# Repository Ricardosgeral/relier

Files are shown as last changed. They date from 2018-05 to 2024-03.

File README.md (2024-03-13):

# *relier - acquisition system*
### Open {*re*}design of an acquisition system for {*l*}aboratory tests on {*i*}nternal {*er*}osion in soils

Project developed by [*Ricardo Correia dos Santos*](https://www.linkedin.com/in/ricardons/) at
[Laboratório Nacional de Engenharia Civil - *LNEC*](http://www.lnec.pt/en/), in Lisbon, Portugal

***relier AS*** is an open 'low budget' acquisition system (hardware and software), that automatically
collects data from multiple analog and digital output sensors, which are commonly used in laboratory tests on soil erosion. 

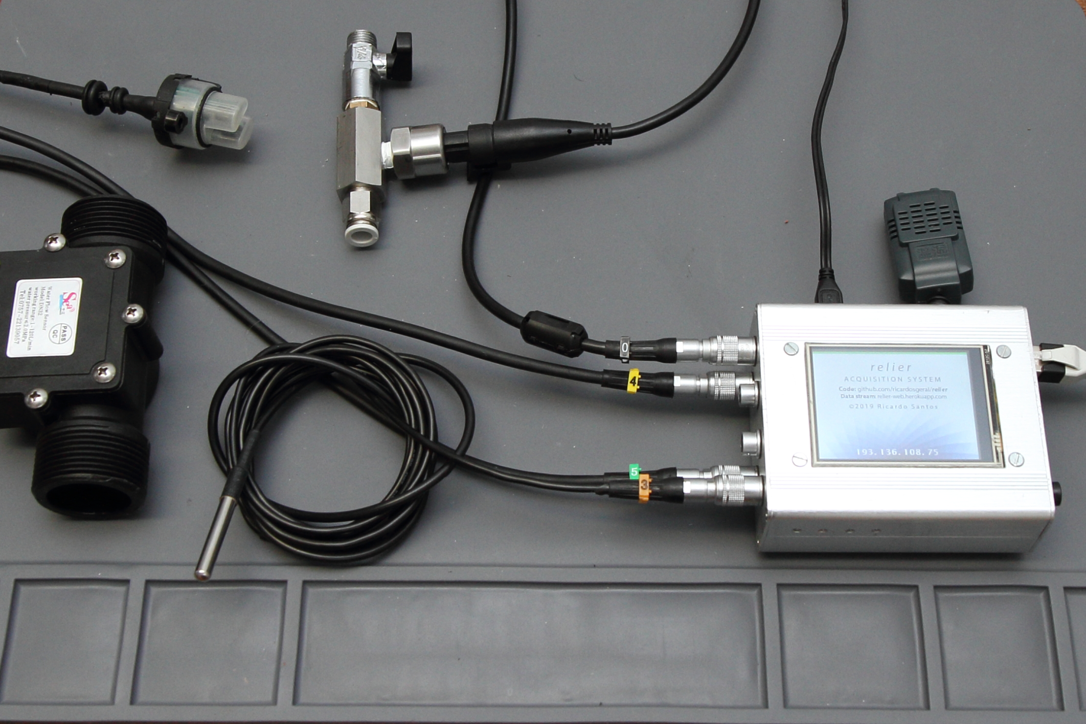
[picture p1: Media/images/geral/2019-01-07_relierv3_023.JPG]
relier


### Some project videos

| Sensors overview and GUI |  Assembly of acquisition system|
|--------------------------|--------------|
| GUI (https://youtu.be/-2fSeosClVY)|  GUI (https://youtu.be/6blSNBFLsIU)                              |

GUI (https://www.youtube.com/watch?v=ju51FE9KWwY)

### Is this for me?
If you need to do a similar project, you just need to have some DIY skills, for scrapping some materials, figuring out 
how to assemble some things together, and investigate how some components work.
The instructions given here should also be taken more like guidelines based on "what I can do with the materials I have". If 
you do not have the exact same hardware components 
(sensors, ADC, level shifter, touchscreen...), yours will surely work a little different, but as they should do the same 
things, there will be similarities too. You may have to adjust the code and/or the connections to meet your needs.

Feel free to contact me if you manage to get it working with different components, so these instructions can be improved 
and be more helpful. 

## 1. Hardware

The hardware components required to make the ***relier*** *acquisition system* are indicated in this chapter. 
Instructions about the way those components are connected are presented.
For reference, some links and prices of each component are indicated.

The *Hardware* is composed by the: 

+ ***Aquisition box*** (*server*, *touchscreen*, *custom PCB HAT* and *connection plugs*);
+ ***Sensors*** (4 with analog outputs and 3 with digital outputs).

### 1.1. Aquisition Box

The main items of the *acquisition box* are the following:
 
 + ***Server***: *Raspberry Pi 3 model B*;
 + ***2.8" Touchscreen***: *Nextion HMI display*;
 + ***Custom PCB HAT***: made specifically for this project ([details about the PCB design](https://github.com/Ricardosgeral/relier/blob/master/README.md#14-custom-pcb-raspberry-pi-hat)).
 
All these main components are placed inside an aluminum enclosure box, in which openings were made, for the power supply, display, and connections. 
Peripheral inputs to collect sensors data, and peripheral outputs (USB ports) to storage sensors data, are also available. 
The acquisition box is powered solely through the power supply connected to the Raspberry Pi (output: DC5V, 2A). 

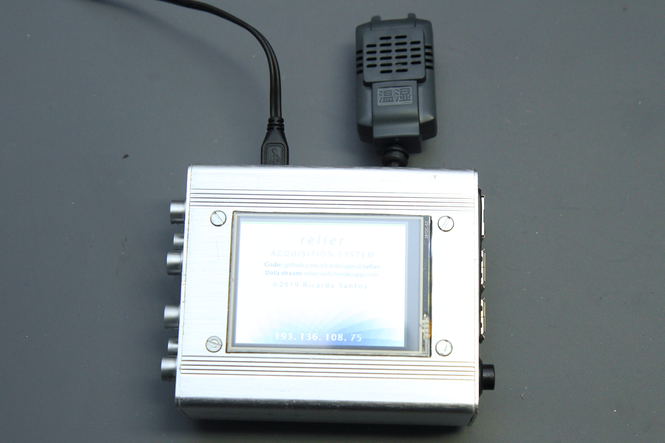
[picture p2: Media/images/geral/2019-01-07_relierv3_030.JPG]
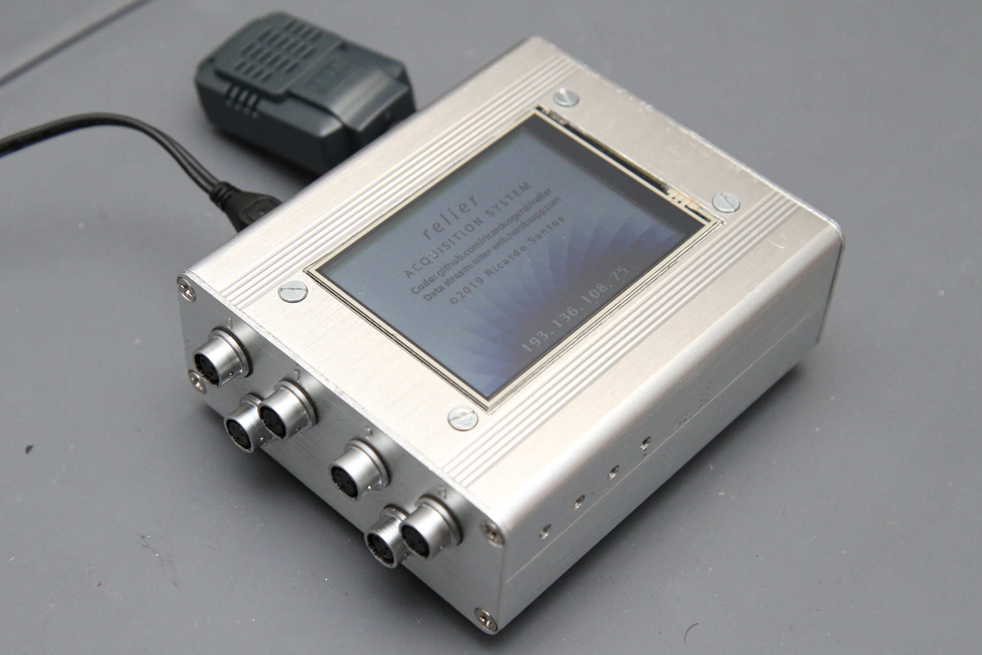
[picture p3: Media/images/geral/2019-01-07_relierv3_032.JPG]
|   |   |
|----------------------------------------|----------------------------------------|
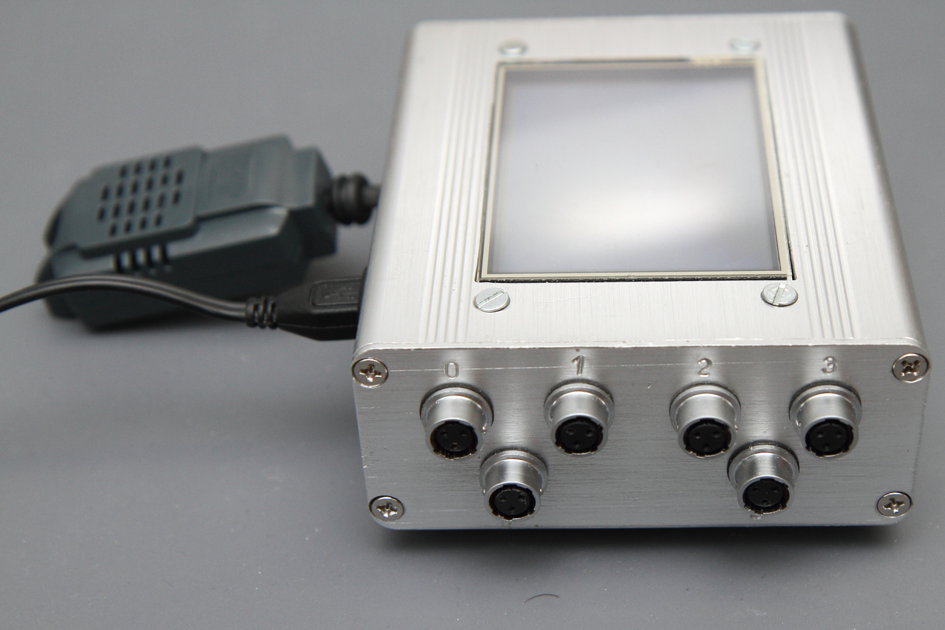
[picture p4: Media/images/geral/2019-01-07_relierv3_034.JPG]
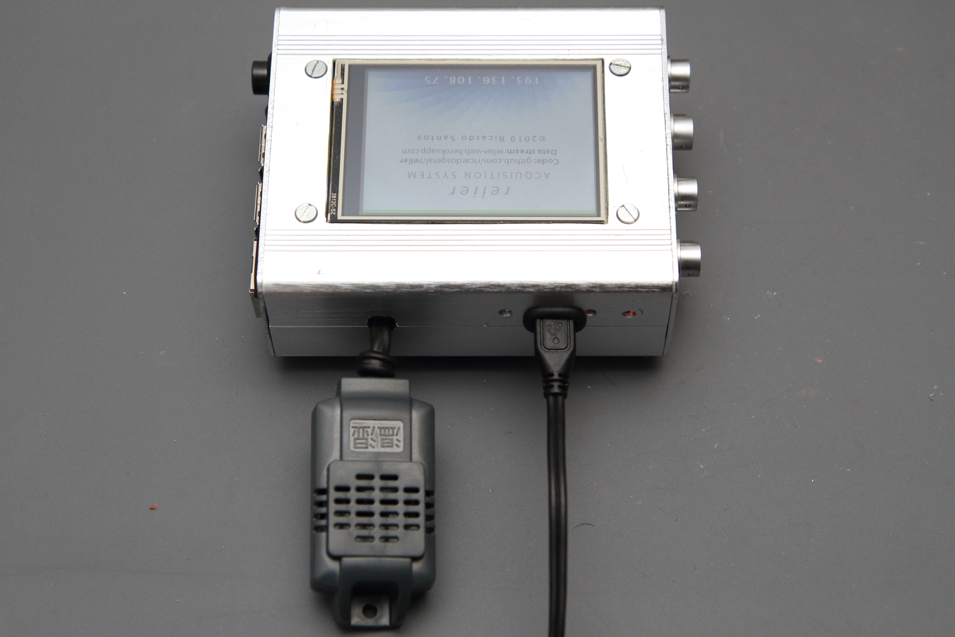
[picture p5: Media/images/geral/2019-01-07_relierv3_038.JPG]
|   |   |
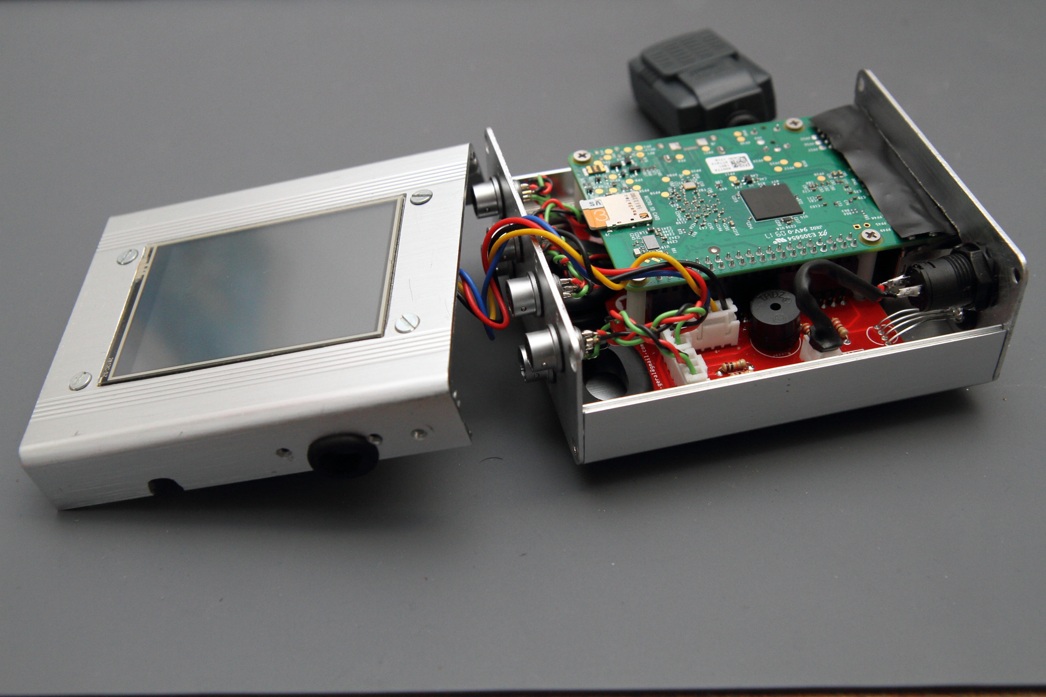
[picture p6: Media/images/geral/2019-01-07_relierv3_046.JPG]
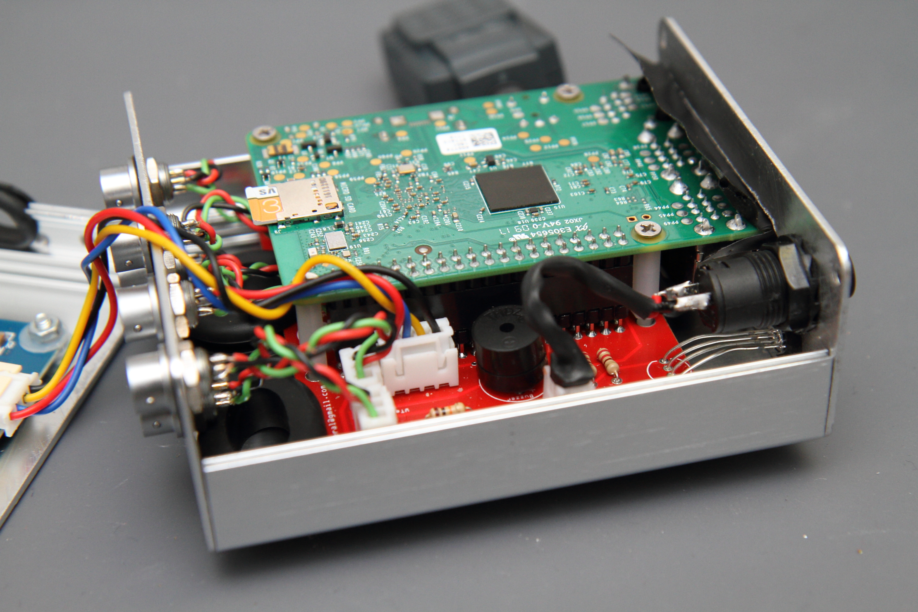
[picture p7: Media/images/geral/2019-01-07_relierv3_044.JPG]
|   |   |

https://i.imgur.com/RYcSZy1.jpg

You can find more pictures and an overview video in the [Media folder](https://github.com/Ricardosgeral/relier/tree/master/Media) of this GitHub repository.

### 1.2. Sensors

The ***relier*** *acquisition system* is prepared to simultaneously collect data from the following ***'low cost' sensors***:

+ **Channels 0-2**    : Analog pressure transducer sensor (Piezometric water pressure);
+ **Channel 3**       : Waterproof DS18B20 Sensor (Water temperature);
+ **Channel 4**       : Analog turbidity sensor (Water turbidity);
+ **Channel 5**       : Turbine flow Sensor (Water flow); and
+ BME280 sensor (Air temperature, humidity and pressure).

Most of the sensors are connected using the 6 mini aviator (circular) plugs that are linked to the custom PCB HAT. 
An exception is the *BME280* chip, which can be soldered directly to the custom PCB or using a short 4 wires cable. 
This last option is preferable, because, ideally, to monitor the ambient air temperature/humidity/pressure, 
the *BME280* should be placed outside the AS box (or at least, inside the box, but near large openings), 
to avoid the heat generated by the touchscreen and by Raspberry Pi!

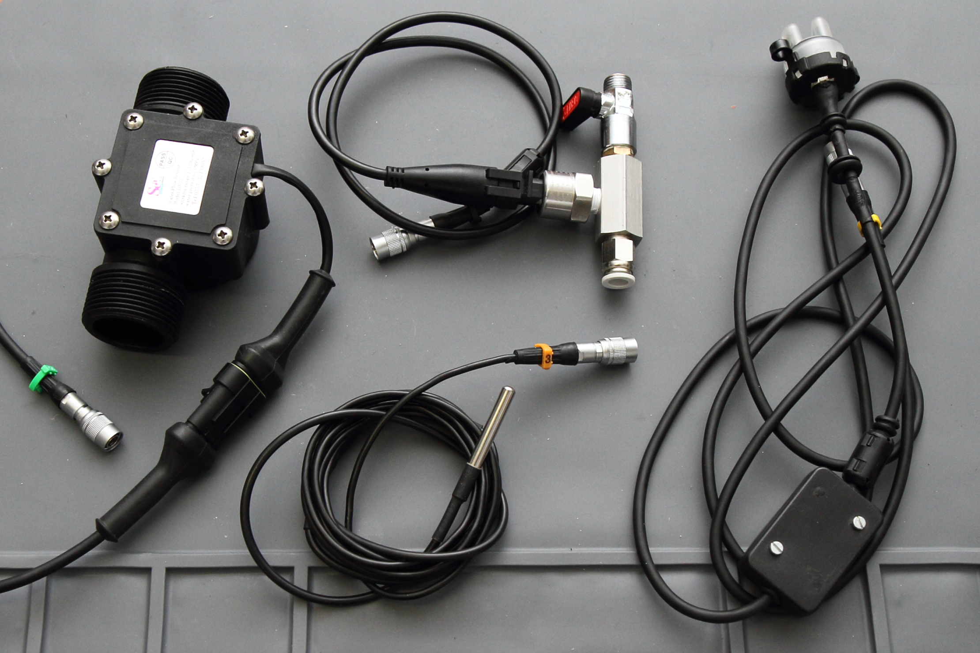
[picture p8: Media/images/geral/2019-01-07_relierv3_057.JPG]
sensors


**Note**:
***relier*** was designed to use low budget sensors. Thus, initially, only allowed the use of a turbine type flowmeter. 
However, since LNEC laboratory owns an Eletromagnetic type flowmeter ([Danfoss MAGFLO 5000](http://apps.watersurplus.com/techlib/Fluidyne/Fluidyne_Flowmeter_Mag1100_Mag3100_spec_D499.pdf)),
the software was adapted to also allow its use (communication via USB serial port of the Raspberry Pi).
Please beware that such devices are much expensive (1500-2000 €) than turbine flowmeters (< 20 €). 
The user should choose, in each test, one of these types of flowmeter.

The following table indicates the advantages and drawbacks of each type of flowmeter allowed. 

**Flowmeter type** |                                        |**Advantages**                                   | **Drawbacks**                                                              |
-------------------|----------------------------------------|-------------------------------------------------|----------------------------------------------------------------------------|
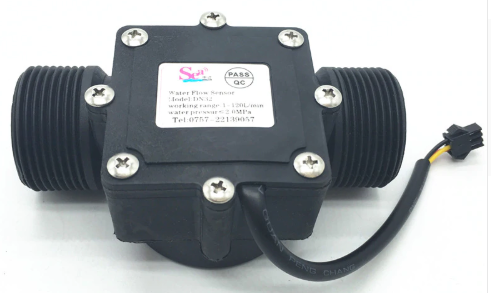
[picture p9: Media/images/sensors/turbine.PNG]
Turbine            |   |Cheap; Fast response to sudden drop/rise of flow | Low accuracy for low flow rates (may be even unable to detect low flow)    | 
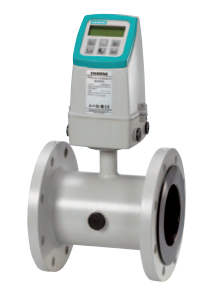
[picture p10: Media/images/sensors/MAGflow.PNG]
Eletromagnetic     |   |Better accuracy, even for low flow rates         | Expensive; Somewhat smother variation of flow, for sudden drop/rise of flow|

### 1.3. Bill of materials (BOM)

The following tables show the bill of materials (BOM) of the items used in ***relier*** **AS**, as well as their main specs and indicative prices (in January 2019).

#### Acquisition Box

| **Qt**  | **€/un*** | **Ʃ €** | **Photo**                                   | **Description**                                                                                                                                                                                                        | Notes                                                                               |
|---------|----------|----------|---------------------------------------------|------------------------------------------------------------------------------------------------------------------------------------------------------------------------------------------------------------------------|-------------------------------------------------------------------------------------|
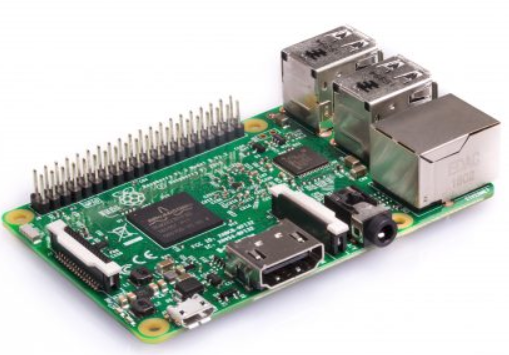
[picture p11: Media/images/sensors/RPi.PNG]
| 1       | 35       | 35       |            |[Raspberry pi 3B](https://www.raspberrypi.org/products/#buy-now-modal)                                                                                                                                                  | Server                                                                              |
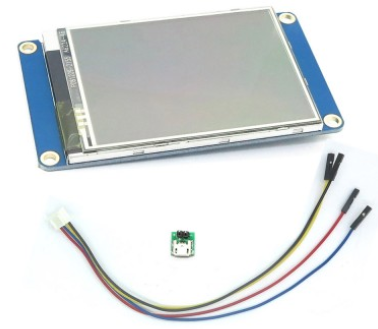
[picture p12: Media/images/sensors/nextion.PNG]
| 1       | 16.2     | 16.2     |        |[Nextion HMI touch display 2.8"](https://www.itead.cc/nextion-nx3224t028-1933.html)                                                                                                                                     | Graphical User Interface (GUI)                                                      |
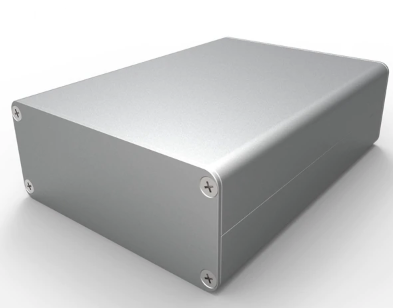
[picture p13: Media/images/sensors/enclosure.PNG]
| 1       | 6.2      | 6.2      |      |[Aluminium enclosure box (88x38x100mm)](https://www.aliexpress.com/item/Free-shipping88-38-100mm-width-x-high-x-length-aluminum-extrusion-box-profile-enclosure-for-PCB/32800855972.html?spm=a2g0s.9042311.0.0.Wvmz38)  | Aluminium enclosure box                                                             |
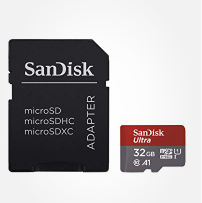
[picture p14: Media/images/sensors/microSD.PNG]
| 2       | 10       | 20       |        |Micro SD card (>16GB)                                                                                                                                                                                                   | One for the raspberry pi and another for the Nextion display (during installation)  |
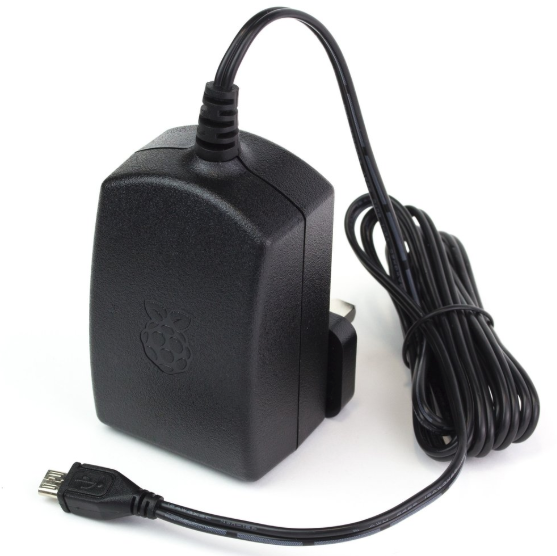
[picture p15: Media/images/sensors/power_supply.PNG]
| 1       | 8        | 8        |   |[Raspberry Pi Power Supply](https://www.raspberrypi.org/products/raspberry-pi-universal-power-supply)                                                                                                                   | Power up the raspberry pi and the sensors                                           |
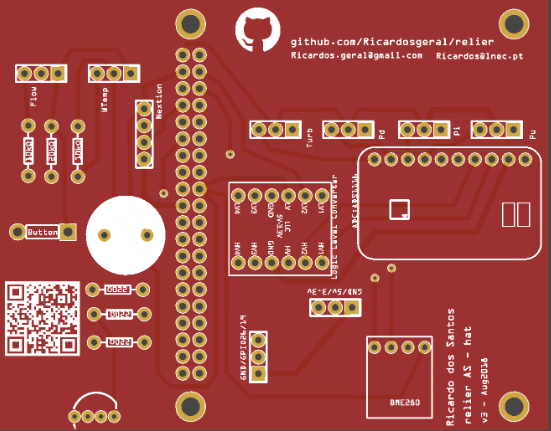
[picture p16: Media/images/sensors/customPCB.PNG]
| 1       | 1        | 1        |      |[**Raspberry pi Hat - Custom PBC**](https://www.pcbway.com/project/shareproject/Relier_Acquisition_system___for_Rasoberry_pi3_b_.html)**:**                                                                             | Interlinks server, touchscreen and the sensors                                      |
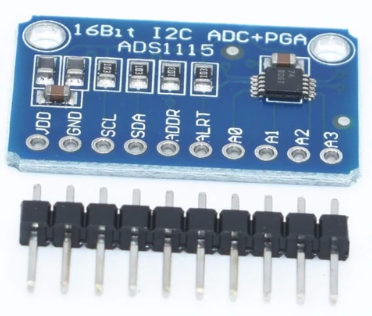
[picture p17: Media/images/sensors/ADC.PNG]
| 1       | 1.4      | 1.4      |            |► [16 Bit I2C ADS1115 Module ADC 4 channel with Pro Gain Amplifier](https://www.aliexpress.com/item/16-Bit-I2C-ADS1115-Module-ADC-4-channel-with-Pro-Gain-Amplifier-RPi-1PCS/32817162654.html)                         | Analog to Digital conversion for analog sensors                                      |
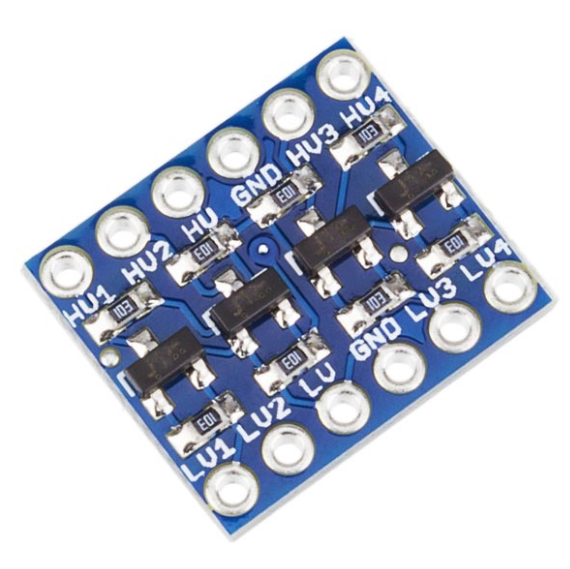
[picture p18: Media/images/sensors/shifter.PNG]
| 1       | 0.3      | 0.3      |        |► [Logic Level Shifter Bi-Directional 5V to 3.3V](https://www.aliexpress.com/item/5PCS-Logic-Level-Shifter-Bi-Directional-For-Arduino-5V-to-3-3V-Four-Way-Two-Way/32827270848.html)                                    | Required for stability, since ADS1115 requires 5V and Raspberry I2C pins use 3.3V    |
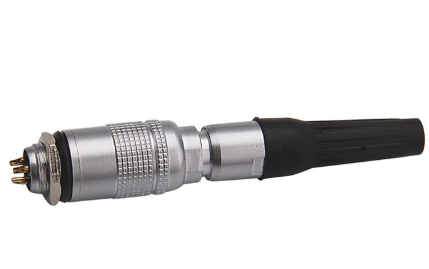
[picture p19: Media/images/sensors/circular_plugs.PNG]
| 6       | 3.8      | 22.8     | |► [8mm Male & Female Connector miniature Aviation Plug M8 Circular Socket+Plug](https://www.aliexpress.com/item/1PCS-AP049-YC8-2-3-4-5-6-7Pin-8mm-Male-Female-Connector-miniature-Aviation-Plug/32845374887.html)      | Connection of the sensors to the acquisition box                                     |
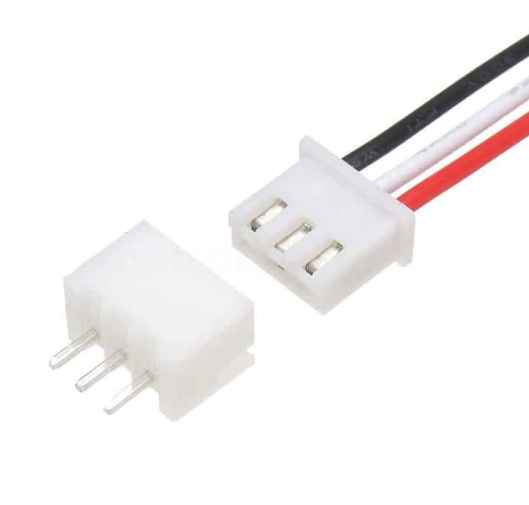
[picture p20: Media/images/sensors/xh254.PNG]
| 6       | 0.2      | 1.2      |          |► [XH2.54 3-Pins connectors Male for PCB - Header+Housing+Terminal](https://www.aliexpress.com/item/XH2-54-2P-3P-4P-5P-6P-7P-8P-9P-10P-11P-12P-13P-14P-15P/32793262315.html)                                           | Connection to the custom PCB                                                         |
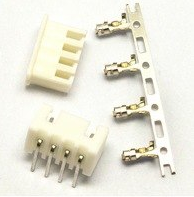
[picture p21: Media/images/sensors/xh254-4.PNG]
| 2       | 0.2      | 0.4      |        |► [XH2.54 4-Pins connectors Male for PCB - Header+Housing+Terminal](https://www.aliexpress.com/item/XH2-54-2P-3P-4P-5P-6P-7P-8P-9P-10P-11P-12P-13P-14P-15P/32793262315.html)                                           | Connection to the custom PCB                                                         |
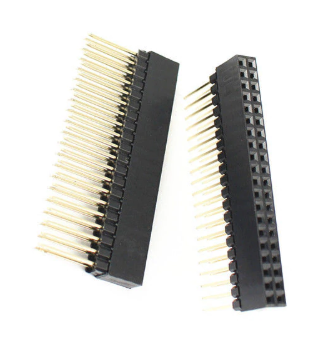
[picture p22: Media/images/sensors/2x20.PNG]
| 1       | 0.9      | 0.9      |           |► [PC104 2.54mm Pitch 2x20 Pin 40 Pin Female Double Row Long Pin Header Strip](https://www.aliexpress.com/item/2-Pcs-PC104-2-54mm-Pitch-2x20-Pin-40-Pin-Female-Double-Row-Long-Pin-Header/32805691836.html)            | Connection between Raspberry GPIO pins and the custom PCB                            |
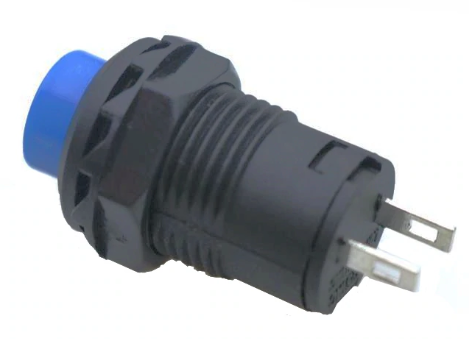
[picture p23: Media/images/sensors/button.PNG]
| 1       | 0.2      | 0.2      |         |► [Momentary pushbutton switch 3A Reset Button](https://www.aliexpress.com/item/10pcs-Momentary-Push-Button-Switch-12mm-Momentary-pushbutton-switches-3A-125VAC-1-5A-250VAC-Reset-Button/32802331189.html)             | Safe restart/shutdown button of the Raspberry Pi                                     |
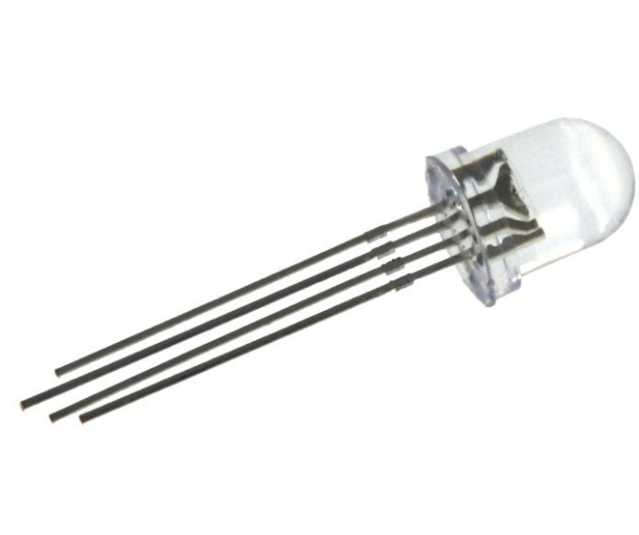
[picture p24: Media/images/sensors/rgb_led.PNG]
| 1       | 0.1      | 0.1      |        |► [5mm Through-Hole RGB LED](https://www.aliexpress.com/item/100pcs-lot-Transparent-Round-5mm-RGB-LED-Common-Anode-LED-Light-Emitting-Diode-Lamp/32278301731.html)                                                     | Indicative multicolor LED                                                            |
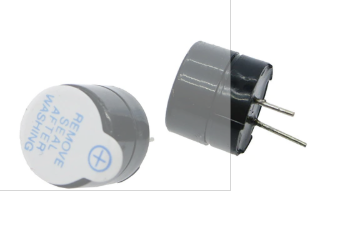
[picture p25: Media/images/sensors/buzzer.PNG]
| 1       | 0.1      | 0.1      |         |► [Active Buzzer Alarm 5 V](https://www.aliexpress.com/item/10pcs-5v-Active-Buzzer-Magnetic-Long-Continous-Beep-Tone-Alarm-Ringer-12mm-MINI-Active-Piezo-Buzzers/32914327679.html)                                     | Audible sound to alert for the end of a test                                         |
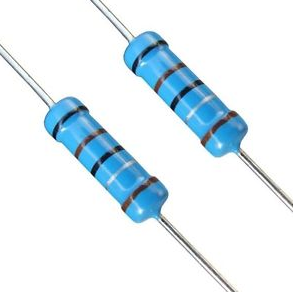
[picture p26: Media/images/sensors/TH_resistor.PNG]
| 3       | 0.02     | 0.06     |    |► [220 Ω carbon film resistor](https://www.aliexpress.com/item/100pcs-1-4W-Metal-film-resistor-1R-1M-100R-220R-330R-1K-1-5K-2-2K/32847011772.html)                                                                     | Protection of the RGB LED                                                            |
| 2       | 0.02     | 0.04     |    |► [10 kΩ carbon film resistor](https://www.aliexpress.com/item/100pcs-1-4W-Metal-film-resistor-1R-1M-100R-220R-330R-1K-1-5K-2-2K/32847011772.html)                                                                     | 1 used as voltage divider (turbine flowmeter) and other for water temperature sensor |
| 1       | 0.02     | 0.02     |    |► [20 kΩ carbon film resistor](https://www.aliexpress.com/item/100pcs-1-4W-Metal-film-resistor-1R-1M-100R-220R-330R-1K-1-5K-2-2K/32847011772.html)                                                                     | Voltage divider (turbine flowmeter)                                                  |
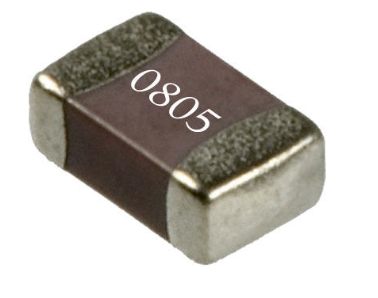
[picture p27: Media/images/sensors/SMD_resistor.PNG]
| 3       | 0.01     | 0.03     |   |► [0805 SMD 1/4W resistor 1MΩ](https://www.aliexpress.com/item/100Pcs-0805-SMD-1-4W-chip-resistor-0R-10M-0-10R-100R-220R-330R-470R-1K/32933956924.html)                                                                | Pull up resistors (to know when analog sensors are disconnected)                     |
| 6       | 0.1      | 0.6      |                                             |► 5 cm cable with 3 wires                                                                                                                                                                                              | Connection between mini aviator plugs and XH2.54 3 pin connectors                    |
| 1       | 0.1      | 0.1      |                                             |► 8 cm cable with 4 wires                                                                                                                                                                                              | Connection between BME280 and the custom PCB                                         |
|         |          | **115€** |                                             |                                                                                                                                                                                                                       |                                                                                     |

*The unitary prices don't include eventual shipping costs. 
For some items, it may be difficult to buy individual components and may be necessary to buy them in sets. 
There may exist cheaper alternatives. The prices indicated correspond to the components bought.

#### Low budget sensors

| **Qt**  | **€/un***| **Ʃ €** | **Photo**                                    |**Description**                                                                                                                                                                                                                    | Notes                                                                                          |
|---------|----------|---------|----------------------------------------------|---------------------------------------------------------------------------------------------------------------------------------------------------------------------------------------------------------------------------------- |------------------------------------------------------------------------------------------------|
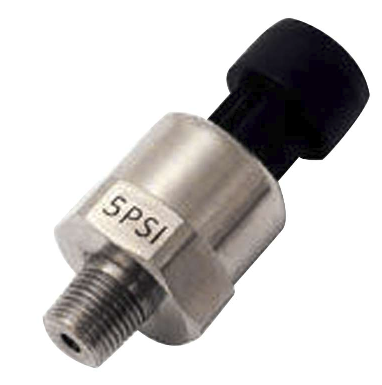
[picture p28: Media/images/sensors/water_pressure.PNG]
| 3       | 13       | 39      |  |[Analog Pressure Transducer Transmitter Sensor, 0-5psi 0.5-5V](https://www.aliexpress.com/item/1Pc-Pressure-Transducer-Sender-Stainless-Steel-for-Oil-Fuel-Air-Water-5psi-CSL2017/32814346612.html)                                | Measurement of water pressure at different levels (piezometers)                                |
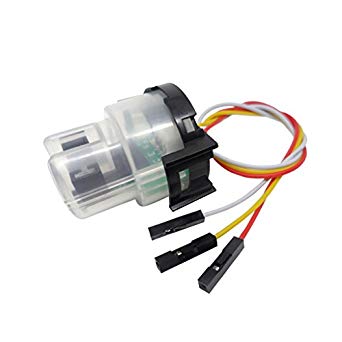
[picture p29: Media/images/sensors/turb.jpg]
| 1       | 9        | 9       |            |[Analog Turbidity Sensor, 5V 40mA](https://www.aliexpress.com/item/DFRobot-Gravity-Analog-Digital-Turbidity-Sensor-5V-40mA-DC-support-both-signal-output-compatible-with-arduino/32595773560.html)                                 | Measurement of the turbidity of effluent water                                                 |
| 1       | 13       | 13      |         |[Digital Turbine Flow Sensor, G5/4, 1.25", DN32, 1~120L/min](https://www.aliexpress.com/item/DN32-Water-Flow-Meter-Sensor-Switch-G5-4-Thread-Port-Industrial-Flowmeter/32567971320.html)                                           | Measurement of the water flow (the system also allows the use a electromagnetic type flowmeter)|
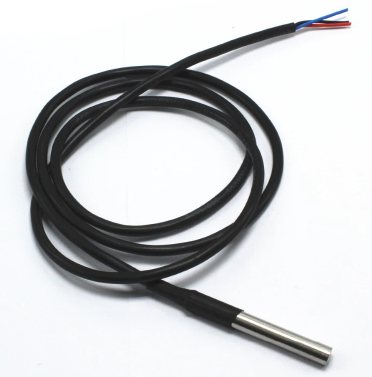
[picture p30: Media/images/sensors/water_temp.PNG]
| 1       | 1        | 1       |      |[Waterproof DS18B20 digital Temperature Sensor](https://www.aliexpress.com/item/1pcs-New-Digital-Temperature-Temp-Sensor-Probe-DS18B20-For-Thermometer-1m-Waterproof/1297739612.html)                                              | Measurement of the water temperature                                                           |
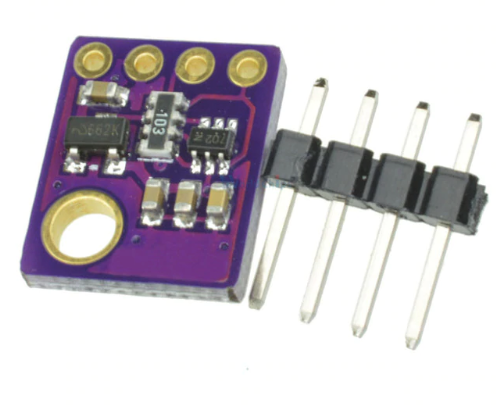
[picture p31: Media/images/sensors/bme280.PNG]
| 1       | 3        | 3       |          |[BME280 Digital Sensor, Humidity, Temp. and Barometric Pressure Sensor](https://www.aliexpress.com/item/3In1-BME280-GY-BME280-Digital-Sensor-SPI-I2C-Humidity-Temperature-and-Barometric-Pressure-Sensor-Module-1/32659765502.html)| Measurement of the atmospheric temperature, humidity and pressure                              |
|         |          | **65€** |                                              |                                                                                                                                                                                                                                   |                                                                                                |                                                                                      |

#### Total cost

The total estimated cost of the ***relier*** **AS** is about **180 €**, considering the use of low budget sensors. 
This value excludes costs related to other supplementary materials required for the assembly of the custom PCB (e.g. solder wire or DIY tools).

### 1.4. Custom *PCB* (Raspberry Pi HAT)
The design of the 2 layer's *PCB* was developed using the open-source software [Fritzing](http://www.fritzing.org/). 
The production files and the *.fzz* file are [here](https://github.com/Ricardosgeral/relier/tree/master/Fritzing). 
Latest version of *PCB* is v3.2 (November 2018). 
The *PCB* was produced/printed by [PCBWay company](https://www.pcbway.com/). 
You can order them a copy [here](https://www.pcbway.com/project/shareproject/Relier_Acquisition_system___for_Rasoberry_pi3_b_.html)).

Below, you can see images showing the circuits hooked in the breadboard and in the PCB, as well as the final 
aspect of each *PCB* layer individually. 
[Here](https://www.raspberrypi-spy.co.uk/2012/06/simple-guide-to-the-rpi-gpio-header-and-pins/#prettyPhoto/1/)
you can see the numbering of the 40 GPIO pins of the Raspberry Pi used.

**PCB: breadboard view**
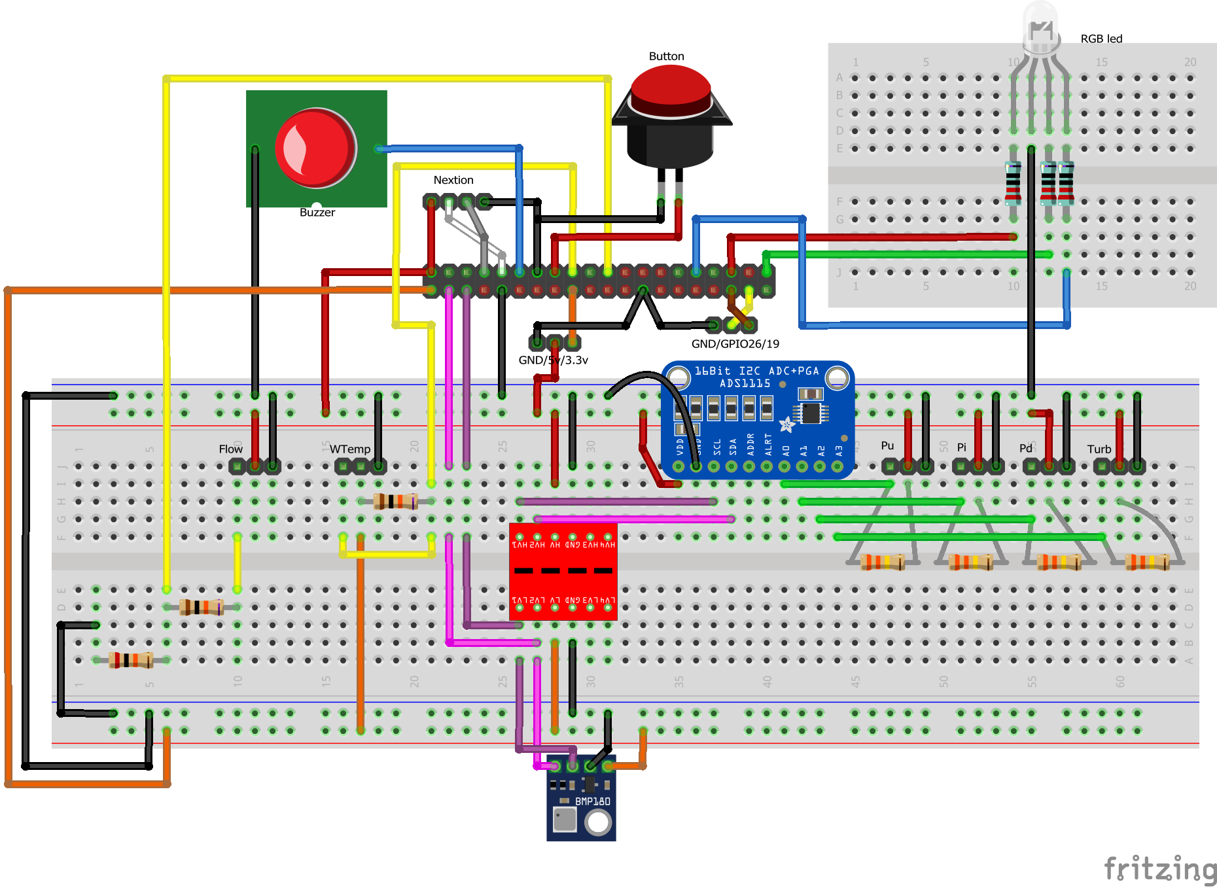
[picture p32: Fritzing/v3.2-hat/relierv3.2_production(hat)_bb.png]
Breadboard_image


| **PCB: bottom Layer**                                           | **PCB: top layer**                                       |
|-----------------------------------------------------------------|----------------------------------------------------------| 
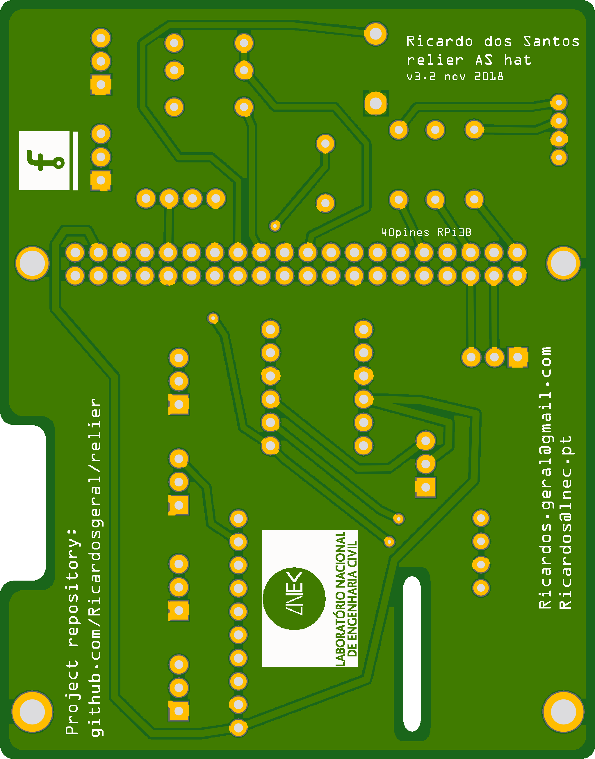
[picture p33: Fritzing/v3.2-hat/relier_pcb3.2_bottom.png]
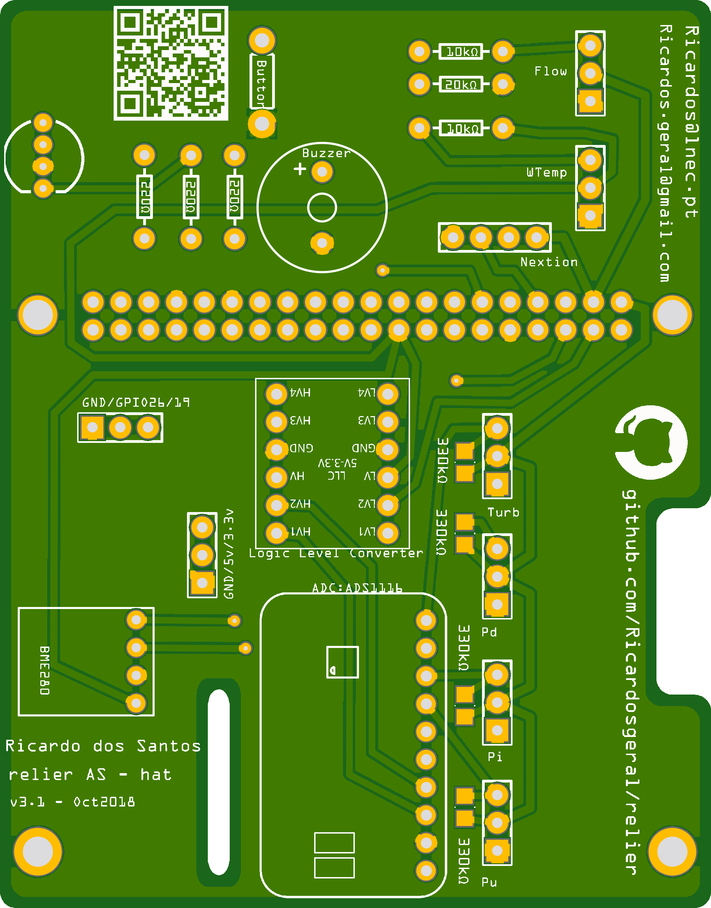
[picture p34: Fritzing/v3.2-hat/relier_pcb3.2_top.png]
|   |  |
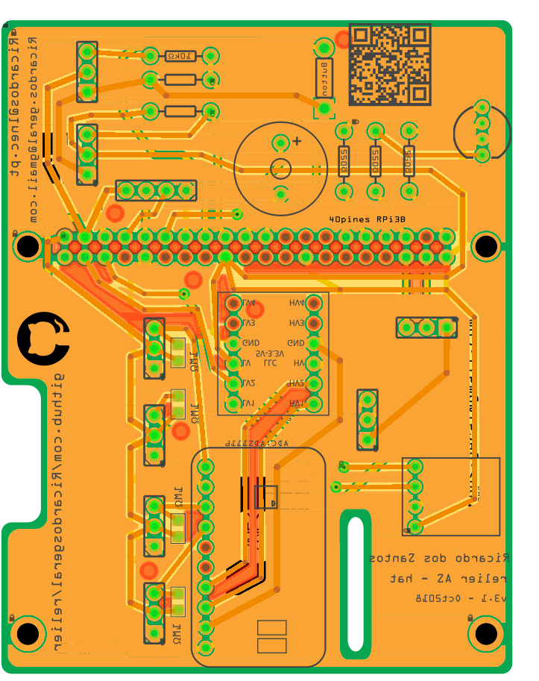
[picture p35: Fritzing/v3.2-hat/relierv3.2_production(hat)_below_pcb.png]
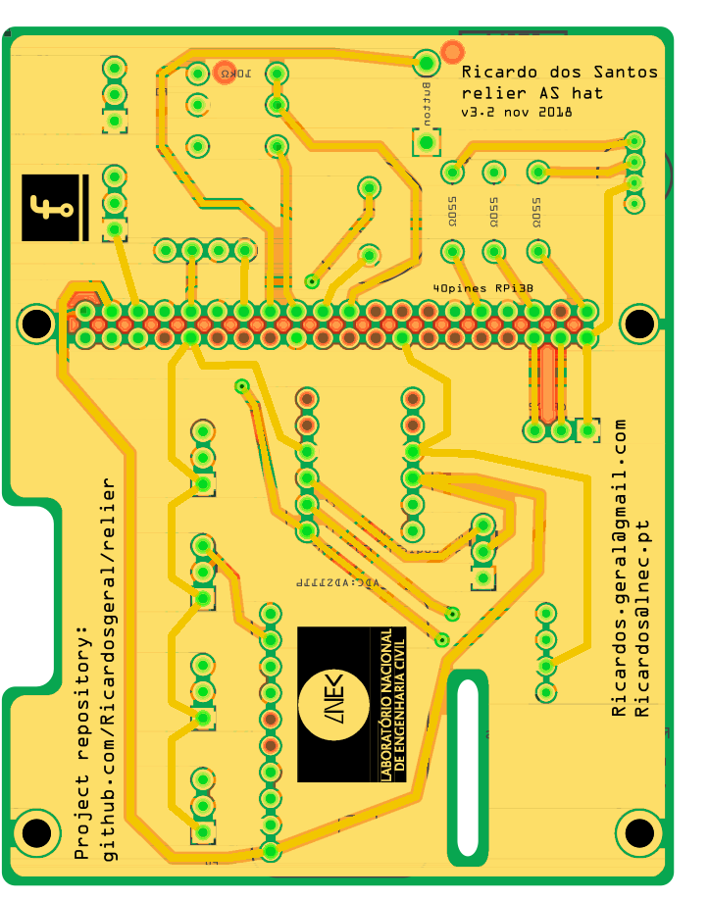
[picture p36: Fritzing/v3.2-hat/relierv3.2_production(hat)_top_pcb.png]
|   | |
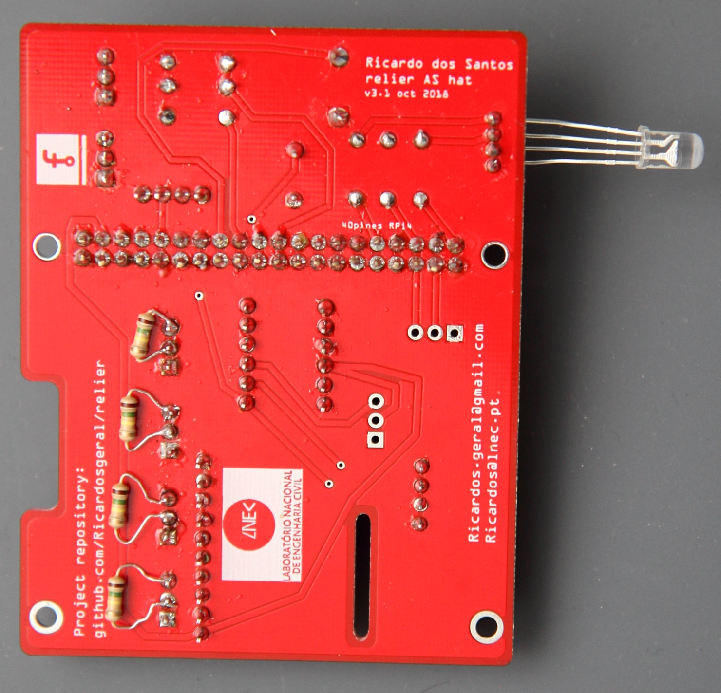
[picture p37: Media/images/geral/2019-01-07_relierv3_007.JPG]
PCBbottom_image
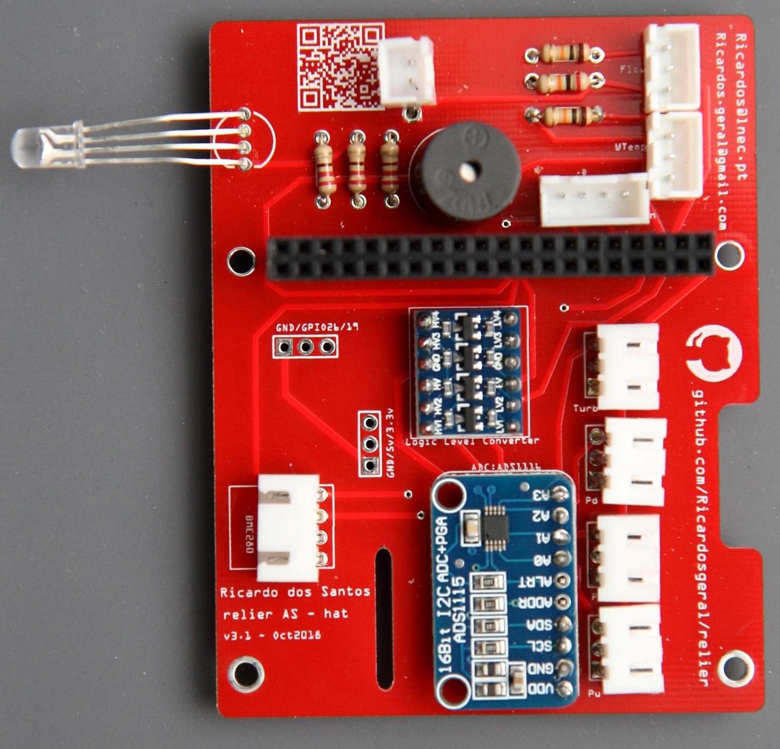
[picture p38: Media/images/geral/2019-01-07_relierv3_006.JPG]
PCBbottom_image
|   | |

**PCB: scheme**
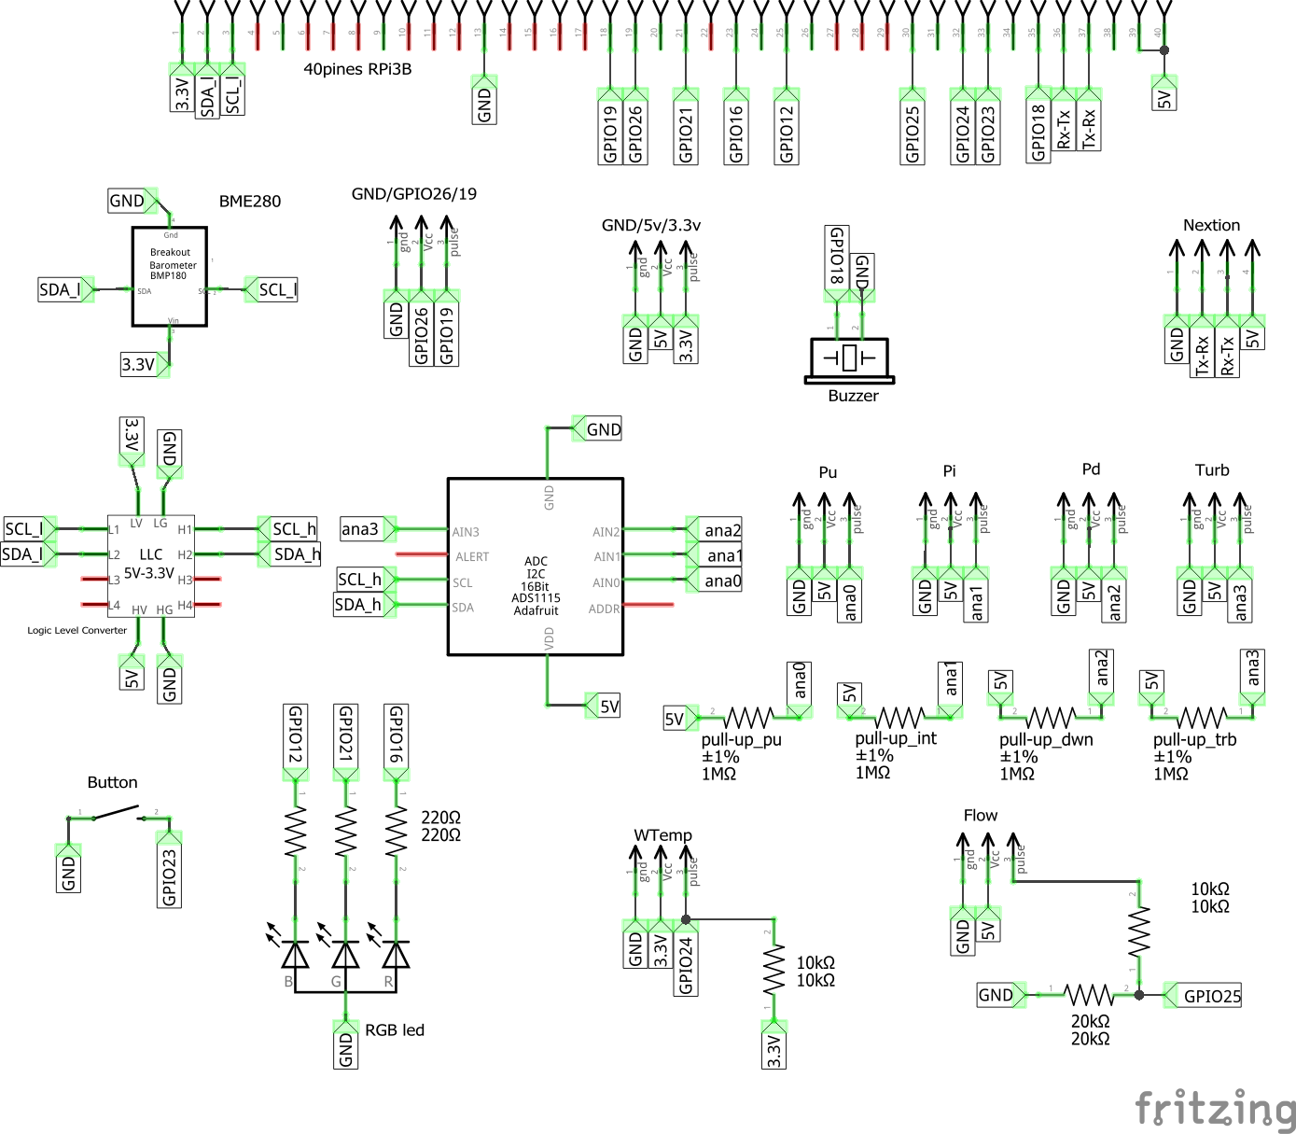
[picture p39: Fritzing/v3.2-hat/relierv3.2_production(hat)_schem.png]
PCB_image


### 1.5. Other components that may be useful for debugging
+ Breadboard(s)
+ [T-cobbler for raspberry pi](https://www.aliexpress.com/item/830-tie-points-MB102-breadboard-40Pin-Rainbow-Cable-GPIO-T-Cobbler-Plus-Breakout-Board-Kit-for/32673580640.html?spm=2114.search0104.3.9.6581309ai8NJdY&ws_ab_test=searchweb0_0,searchweb201602_1_10152_10151_10065_10344_10068_10342_10343_5722611_10340_10341_10698_10696_5722911_5722811_10084_5722711_10083_10618_10304_10307_10301_5711211_10059_308_100031_10103_10624_10623_10622_10621_10620_5711311_5722511,searchweb201603_32,ppcSwitch_5&algo_expid=3ed88c37-67f1-4fe2-a688-b3983db90ff7-1&algo_pvid=3ed88c37-67f1-4fe2-a688-b3983db90ff7&transAbTest=ae803_2&priceBeautifyAB=0)
+ DuPont jumper wires
+ Micro SD adapter
 
### 1.6. Additional tools required in the assembly of the Raspberry Hat and of the enclosure
+ Wire Stripper/Crimping tools
+ Soldering iron + solder wire
+ Tools to make the openings in the aluminum box (*eg* a mini Drill DIY set) 
+ Precision screwdriver set

## 2. Software

The  ***relier*** *acquisition system* is composed by two distinct but interconnected programs, particularly the:

+ **Server software**: *runs in the Raspberry Pi*, and performs the computation tasks, and
+ **Touchscreen software**: *runs in the Nextion device*, and is responsible by the interactivity between the end user and the server.

### 2.1. Server software: installation
The server is a Raspberry Pi 3 model B (it was also tested successfully with a RPi 3 B+).
 These instructions should be carried out after a fresh installation of *Raspbian* image in a Micro SD card 
(see [instructions](https://www.raspberrypi.org/documentation/installation/installing-images/README.md)). 
The server has been tested with [2018-11-15-raspian-stretch](http://downloads.raspberrypi.org/raspbian/images/raspbian-2018-11-15/). 
Most of the code is written in *Python v3.5.3*, and a few scripts are written in *Bash v4.4.12(1)*.

**Note:** If no monitor is available (*Raspberry Pi* headless setup), the following 4 simple steps are required to 
enable *SSH* on first boot. So, right after installing the Raspbian image in the  Micro SD card:
1. Create an empty file (in Windows use notepad, in a Linux terminal use command *touch*, in Mac use TextEdit).
2. Save the file with name: ***ssh*** (preferentially with no extension, but *ssh.txt* should also work).
3. Copy or move that file into the ***root*** of the Micro SD card, where Raspbian image is installed.
4. Insert the Micro SD card into the *Raspberry Pi*, and power it on.

Access the *Raspberry Pi* directly (if you have a monitor), or via *SSH* (for example, using [*Putty*](https://www.putty.org/)). 
In this last option, you will require an internet connection, and need to know the local IP attributed to the *Raspberry Pi* ! 
The default login parameters should be:

   username: `pi`   
   password: `raspberry`

It is recommended to change the password after first boot, since *SSH* is enabled! For that write down in the terminal

    $ passwd 
    
and choose your new password.

Now, if you haven't done it yet, you need to connect the *Raspberry Pi* to the internet (via Ethernet cable or [WiFi](https://www.raspberrypi.org/documentation/configuration/wireless/wireless-cli.md)).  
Then, in the terminal, run the following sequential commands:
    
    $ cd /tmp && wget https://raw.githubusercontent.com/Ricardosgeral/relier/master/bash/raspbian-post-install.sh
    $ sudo chmod +x raspbian-post-install.sh && sed -i 's/\r//' raspbian-post-install.sh
    $ sudo ./raspbian-post-install.sh

Prepare a big cup of hot tea, since this can take some minutes! The raspberry should reboot automatically!

**Note:** During installation of the server, [VNC](https://www.realvnc.com/en/raspberrypi/) is also enabled, 
case you want to use it. 

#### Google Credentials

***relier AS*** has the ability to send the main test results to google sheets, but, for that, it requires some configurations.
If you don't need this feature you can skip it.

After reboot of the RPi, you need to get your *json* file with your Google Signed credentials.
First, you need to create a project in the developer console and enable some APIs (follow steps 1 to 4 from these [instructions](https://pygsheets.readthedocs.io/en/latest/authorizing.html#)), 
then, get the *Signed credentials* (follow steps 5 and 6 from these [instructions](https://pygsheets.readthedocs.io/en/latest/authorizing.html#signed-credentials)). 
*Copy* your Signed credentials, then, do:

    $ sudo nano /home/pi/relier/service_creds.json
    
and *Past* the Signed credentials. `Ctrl+X`, then `y` and finally `Enter` to save file.

    $ sudo reboot

And that's it, after reboot, the *Raspberry Pi* is set properly. 
However, you still need to install the **Touchscreen software**!

### 2.2. *Touchscreen* software: installation

The graphical user interface (GUI) runs on a [*Nextion*](https://nextion.itead.cc/) smart touchscreen, 
also referred as an *HMI - Human Machine Interface*. 
Note that, this device does not work like typical TFT or HDMI monitors. 
A code needs to be developed and uploaded to the device using a Micro SD card. 
The connection between *Nextion device* and the *Raspberry Pi* is made via 
[*Serial UART*](https://www.allaboutcircuits.com/technical-articles/back-to-basics-the-universal-asynchronous-receiver-transmitter-uart/), 
that is, via serial communication in pins GPIO14 (TXD) and GPIO15 (RXD) (in all Raspberry models).

The GUI needs to be developed in the [Nextion Editor](https://nextion.itead.cc/resources/download/nextion-editor/) (free software - only for windows!).
Follow the [Nextion Editor Guide](https://nextion.itead.cc/editor_guide/) to learn how to work with it. 
I've provide the file [*relier.HMI*](https://github.com/Ricardosgeral/relier/blob/master/Nextion/HMI/relier.HMI) 
developed for this project. The next picture shows the Nextion Editor with the project file.

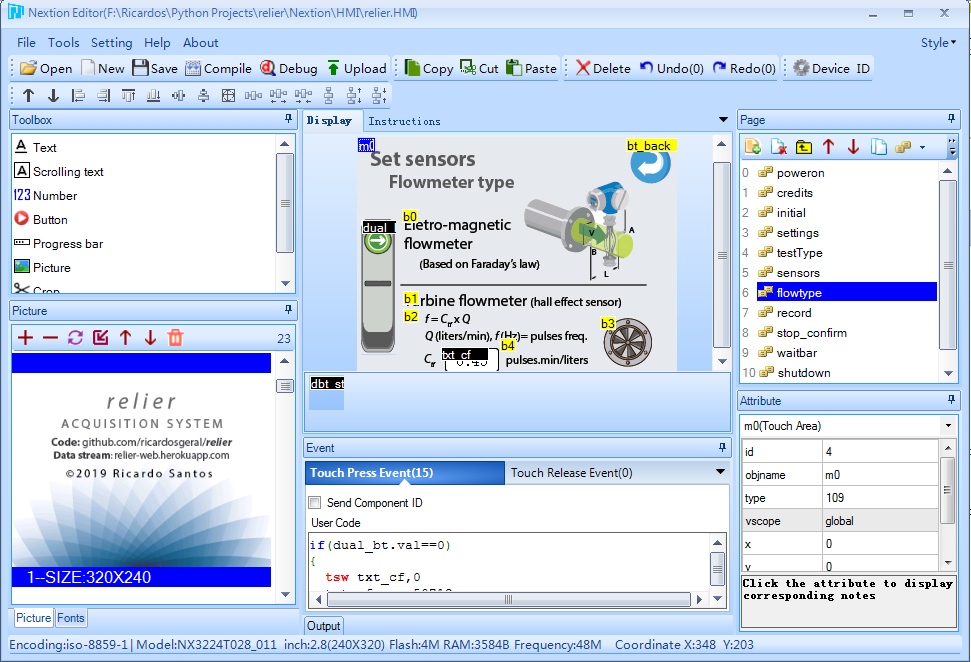
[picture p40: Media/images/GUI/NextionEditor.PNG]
NextionEditor


To upload the code into *Nextion device touchscreen* follow these steps:

1. Open the [*relier.HMI*](https://github.com/Ricardosgeral/relier/blob/master/Nextion/HMI/relier.HMI) file
with the Nextion Editor.
2. Press the *Compile* icon in the first top bar, and check that there are no errors.
3. Go to *File > Open build folder* and copy the *relier.tft* file produced by the editor (that has the code). 
4. Past the file into a formatted micro SD card. I recommend using the windows format tool, 
to ensure the card is empty. Don't forget to safe eject the sd card.
5. Disconnect the power supply to *Nextion*.
6. Insert the micro SD card in the slot on the back of the device.
7. Reconnect the power supply to *Nextion*. You should see the *SD card update* status. 
When you see `Check data.. 100%`, the code was uploaded successfully.  
8. Disconnect again the power supply to the screen, and remove the micro SD card (it will not be necessary anymore).
9. In next start up, the software with the code, developed in the Nextion Editor, is running 
and the GUI is set on the touchscreen.

**Note:** Be very careful when buying the *Nextion* device. Confirm that you are not getting a *TJC* (for the Chinese market), 
which looks identical. 
*TJC* screens only work with the Chinese version of the Nextion Editor! You will need to learn Chinese to use it !!!!

## 3. Graphical User Interface (GUI): How to use
 
The *GUI* pages displayed in the touchscreen (*Nextion device*), and their usage, are shown next.
 
### *Connecting* page
page0

Right after a start up or reboot of the *Raspberry Pi*, you should see this **Connecting** black page. 
Waiting a while (tipically 20 seconds, but can vary from 15 to 60 seconds, depending on the pending OS services) 
you should see the **Credits** page. 
In that process you should see fast blink of the led (with purple color) placed in the AS box.

### *Credits* page

First, you will see a *red* flag on the top of the screen. Wait (less than 5 seconds).
After some server checks, the flag should then stay *green*, meaning that the server and touchscreen are working Ok. 
You can also see the local *IP address* of the server, 
which is useful in case you want to make a remote connection. 

| *not ready*: red flag                                    |  *ready*: green flag                                      |
|----------------------------------------------------------|-----------------------------------------------------------|
| page1_red | page1_green|

If the server is not connected to the internet, then the following message is displayed: `No internet connection`.

To update the IP status case the internet connection has been changed (e.g., insertion of an Ethernet cable, connection to WiFi, ...), 
wait a couple of seconds, then touch on the IP message (bottom of the screen). 
Touch anywhere else on the screen to go the **Main menu** page.
 
### *Main menu* page
page2
 
You have three options:
 1. ***Settings***: set the *test inputs* >> Redirects to **General settings** page.
 2. ***Sensors***: set the *calibration inputs* of water pressure sensors and choose flowmeter type >> Redirects to **Set sensors** page.
 3. ***Start***: initiate the test right away >> Redirects to **Sensors data record** page.
 
You can skip options 1 and/or 2, case you use the files
[*inputs.ini* ](https://github.com/Ricardosgeral/relier#5-inputs-file-inputsini), 
[*calibturb.txt*](https://github.com/Ricardosgeral/relier#calibturbtxt-file)
and you are confident that the calibration
parameters of the pressure sensors, specified in that file, are accurate enough. 
 
### *General settings* page
page3

Here, you can edit interactively the test inputs:
- *CSV filename* textbox - name of the CSV file were test data is saved.
- *Google Sheets* checkbox - select it, to send test data to Google Sheets during the test. Disable it if you haven't configured the google credentials.
- *Spreadsheet* textbox - name of the Google spreadsheet (worksheet name = *CSV filename*). Not used if *google sheets* checkbox is disabled.
- *email* textbox - email to where a link, to access the Google spreadsheet, will be sent. Not used if *google sheets* checkbox is disabled.
- *Test time* textbox - duration of the test, in minutes ( if 0 is selected → records data 'forever' or until user stops it).
- *Record* textbox - interval between records, in seconds.
- *Number* textbox - number of readings in each record interval (for analog outputs only).

Pressing the blue button on top-right corner goes back to **Main menu** page. 
There is also a blue button that allows the user to select the **Test type**.

### *Test type* page
page4

This page allows the selection of the type of test you want to perform.
Note that, selecting the option <Hole Erosion Test (HET)>,
***no*** data of the interface (middle) pressure sensor will be acquired, 
since HET only uses two pressure sensors (upstream and downstream).
If you select <**Other**>, a textbox is enabled for the user to give a name to the test type. 
In this case, test data from all sensors is recorded.

To go back to the **General settings** page, click the blue return button. 

### *Set sensors* page
page5

This page allows to see the sensor data (piezometric pressure, flow and turbidiy), which should be displayed every second.

It can also be used to set the calibration parameters of the analog pressure sensors and of the turbidity sensor. 

For the pressure sensors a linear relation, between the analog readings and the effective measurements, is assumed. 
***m*** and ***b*** are the calibration parameters.

The calibration of turbidity is made *exclusively* using the file *turbcalib.txt*. 
First line of this file is ignored and values should be separated by tab or spaces. 
Decimal separator should be a point (.), **not** a comma (,).

To edit the file, open a terminal and type:

    $ sudo nano /home/pi/relier/turbcalib.txt 

The following table indicates the units that should be considered for the calibration parameters.

| Sensors             | ***x*** (analog from ADC)    | ***y*** (measurements) | Relation y = f(x)      |
|:--------------------|:-----------------------------|:-----------------------|------------------------|
| Pressure transducer | voltage,V (*Volt*)           | pressure, p (*bar*)    | ***p = m V + b***      |
| Turbidity           | 0 to 32767 (15 bits >> 2^15) | turbidity (gr/liter)   | ***turbcalib.txt***    |

This page also includes:

a) ***Calibration* button**: to update readings after setting new input parameters.

If you modify  the *m* and *b* parameters of any of the sensors, you need to push the *Calibration* button, 
in order to see the influence on the pressure and/or turbidity values. 

b) ***Zeroing* button**: to make current sensor pressures equal to zero.

This functionality can be used to take into account the normal variations of the atmospheric conditions and the normal sensors drift over time.
To use it properly, it is necessary, first, to ensure that *no pressure* is applied to the sensors (besides the ambient pressure).

In such conditions, ideally, the readings from the pressure sensors should indicate null *mbar*. 
However, due to the influence of drift, barometric pressure, ambient temperature, humidity, and others, 
the most likely is that they are not zero. 

If you push the *Zeroing* button at this stage (*ie*, with no external pressure applied), 
you will get a *wait a few seconds* progress bar. After a few seconds, the readings will show up again,
and show the corrected values.
Now the piezometric pressures should be nearly null. The next figure exemplifies the '*zeroing*' procedure, 
which is done in all pressure sensors simultaneously.

zeroing

***Attention***: the '*zeroing*' process (when desired!) should be done at the beginning of each test, 
 since the history of the zero shift, *z*, is not (intentionally) remembered by the acquisition system after reboot. 

When you consider that the pressure sensors are conveniently calibrated, you can press the *back blue button* (top-right), 
which will send you to the **Main menu** page.

Pushing the *Home* button will send you to the **Credits** page.  
Pushing the *flowmeter icon* button will redirect the user to the ***Flowmeter type*** page 

### *Flowmeter type* page

This page allows to select between a turbine flowmeter and an Eletromagnetic flowmeter.

page6

If a turbine flowmeter is selected, the parameter ***Ctf*** should also be indicated (default value is 0.45).  
*f = Ctf x Q*, where *Q* (liters/min) is the flow rate and *f* (Hz) are the pulses frequency. 

Pressing the *back blue button* will bring the user back to ***Set sensors*** page, 
and changes to the flowmeter type are reflected in the flow rate value.

### *Sensors data record* page
page7

This page appears once the *Start* green button in **Main menu** is released. 
After a couple of seconds, the data being recorded appears in the screen and is updated at a constant rate (*interval* input parameter).

If 'Google Sheets' option has been selected, the first reading can take more than normal (due to the request to access the Google API).

Each time the acquisition system records a set of values, the LED will blink with a green color.

If you want to stop the test, prior to the test duration defined in settings, 
just press the *Red button*, which performs one more reading and then will redirect 
the user to the **Stop recording** confirmation page.

When the predefined test duration is achieved, the server stops acquiring the data. 
The buzz emits some sounds (SOS in morse code! :) ), and the screen is redirected to the *Credits* page.

**Note:** if you want to record data 'forever', set the *Test time duration* input parameter to **0**. 
Actually, it will not record indefinitely. *'Forever'* should be understood as 2 months (86400 minutes!).

### *Stop recording* page
page8

Here you confirm that you pressed the stop button, just in case! Pressing the:

- *Green button* >> stops recording data and directs to **Credits** page. 
- *Red button*   >> go back to **Sensors data record** page, and readings never stopped being registered.
 Buzzer should also alert for the end of the test.

### *Shut down* page

When the physical push button at the lateral side of the acquisition box is hold longer than 3 seconds, the Raspberry Pi shut downs automatically.

page9 

The user should unplug the power supply, after some seconds (> 10s).

## 4. Web live streaming of data from sensors

In GitHub repository [relier-web](https://github.com/Ricardosgeral/relier-web) 
you can find all the required files to deploy a *Python* application to the internet that allows web streaming of the test data recorded.
In that way you can live view the test results acquired by ***relier*** from any device connected to the internet 
(smartphone, tablet, laptop, ...). 
The acquisition system server should be connected to the internet before the start of the test.  

The picture below shows the the app layout, which is accessed at the site ***https://APP_NAME.herokuapp.com*** (you should choose the <APP_NAME>)
 
relier-web

## 5. Inputs file: *inputs.ini*

It is possible to set most of the test inputs by editing the file [*inputs.ini*](https://github.com/Ricardosgeral/relier/blob/master/inputs.ini). 
Editing the file avoids setting the inputs interactively in the touchscreen. 
For that, open a terminal and run the command:

    $ sudo nano /home/pi/relier/inputs.ini
     
and change the parameters as intended.

The structure of the *inputs.ini* file comprises 6 sections: [settings], [testtype], [analog], [flowmeter], [ip] and [path]. 
The last two sections are informative only, thus, their edition don't produce any effect!
An example of an *inputs.ini* file, with a description of the meaning of each parameter, is shown below.

#### Example of file *inputs.ini* 
```
[settings]
filename      = soil_X_n01   # <Name of the CSV file> and (if google_sheets = yes) <Worksheet of Google Spreadsheet>
google_sheets = yes          # <yes (y, yep, Yes, YES) or no (n, nop, No, NO)>  
googlesh      = tests_soilX  # <Name of the Google spreadsheet>
share_email   = my@email.com # <email to share access to the Google spreedsheet>
duration      = 180          # <Duration of the test in Minutes> duration = 0 will run 'forever'
interval      = 15           # <Interval between records in seconds>
no_reads      = 5            # <Number of readings per interval (analog sensors only)>: 
                             #  In this example an average between 15/5=3 values is made.

[testtype]
testtype      = 1            # <1 to 4>  1-HET; 2-FLET; 3-CFET; 4-OTHER
othername     = other_name   # < Name of the test type> only relevant when testtype = 4

[analog]                     # Equation of the straight lines for pressure sensors: y = m x + b
mu            = 0.0862       # <Upstream pressure sensor> [ pu(bar) = mu tension_u(Volts) + bu ] 
bu            = -0.0432
mi            = 0.0898       # <Interface pressure sensor> [ pi(bar) = mi tension_i(Volts) + bi ]
bi            = -0.0432
md            = 0.0898       # <Downstream pressure sensor> [ pd(bar) = md tension_d(Volts) + bu ]
bd            = -0.0432

[flowmeter]                  # Parameters about the flowmeter type
flowmeter_type = 1           # < 1 or 2> 1-Eletromagnetic;   2-Turbine  
cf = 0.45                    # Calibration parameter for the turbine flowmeter

[ip]
lastip     = 193.136.108.75  # Parameter is not editable! It's an indication of the server IP in the last test 

[path]
lastpath   = /srv/EROSTESTS/soil_Y_n01.csv  # Location where the results of the previous test were stored.
```

#### Additional notes

+ If the user changes the parameters in the interactive way, [*inputs.ini*](https://github.com/Ricardosgeral/relier/blob/master/inputs.ini) 
will be updated every time the, 
  + server begins to record data (green start button in **Main menu**), or
  + blue back button is released in **Set sensors** page.
+ In such cases, the parameters are kept and are set by default in the next test.
+ Note that the parameters in the *ini* file will not appear always in the same order! 
However, they will always appear in their respective sections. 
That is, for example, the parameter *interval* will always appear in section [settings], 
but may appear at any position inside its section.

## 6. Turbidity calibration 

The calibration of the turbidity sensor is made mixing successive portions of soil with a know quantity of water. 
The water used in calibration should of the same nature and chemistry of the one that will be used in the soil tests. 
The liquid should be agitated during all the calibration process, to avoid sedimentation of any suspended particles. 
This can be achieved easily using a portable magnetic stirrer. 

Since the turbidity probe is not waterproof, a calibration cup has been designed for safety reasons. 
The design of this calibration cup is available in [Thingiverse](https://www.thingiverse.com/thing:3299997). 
The calibration cup shown in the pictures below was 3D printed in PLA material. Feel free to (re)use the design.

|   |   |
|---|---|
|turbcalib | turbcalib|

**Procedure/Steps**

The steps and best practices to achieve a consistent calibration curve for the turbidity sensor are here presented. 
Below are some photos taken during the calibration for the finer fraction of a coarse soil (passing sieve #60, aperture of 6.3 mm)

|turbcalib |turbcalib |
|-----|------|
|turbcalib |turbcalib|

These are the main steps:
1. Place a know quantity of water (e.g. 500 ml) inside a beaker.
2. Place the beaker over a portable magnetic stirrer. Turn it on, and regulate the spinning in a way that the water is agitated, but without forming a visible vortex.
3. Place the calibration cup (with the sensor) floating in the water.
4. Connect the turbidity sensor to Channel 4 in the acquisition box, and start the system (i.e. connect the RPi to the power supply).
5. Register ***analog#*** of this channel. The register of this values can be done:
    + *Manually* - Navigate to [*Set sensor*](https://github.com/Ricardosgeral/relier/blob/master/README.md#set-sensors-page) page, 
and register the values shown in the turbidity section;
    + *Automatically* - Navigate to [*Sensors data record*](https://github.com/Ricardosgeral/relier/blob/master/README.md#sensors-data-record-page) page, 
and the ***analog#*** values are recorded to the adequate file (see [Data collection](https://github.com/Ricardosgeral/relier/blob/master/README.md#7-data-collection) section).  
6. Add a known mass of the selected soil (e.g. 0.1 grams) to the stirring water. Wait a fee seconds, and then register the new ***analog#*** values,
 which are expected to be smaller than those before adding the amount of soil.
Calculate the turbidity in grams/liter, dividing the cumulative mass of the soil by the total amount of water (e.g. 0.1 grams/0.5 liters = 0.2 l/g).
7. Repeat step 6 until the entire range of possible turbidity's is tested. As reference, it is considered that calibration process is finished when analog# is below 1000. 
8. Modify the file *calibturb.txt* with the tested pairs of *analog#* versus *turbidity* (g/l). This procedure is indicated next.

### Edition of *calibturb.txt* file

The file *calibturb.txt* allows to define a calibration curve for the turbidity analog sensor. 
For that, open a terminal and run the command:

    $ sudo nano /home/pi/relier/calibturb.txt

Pairs of **analog number** (0 to 32767) versus **turbidity** (grams/liter) should be introduced.

### Example of file *calibturb.txt* 
```
Analog#  grams/liter   # The first line is always ignored
29618	0
29586	0.025
29430	0.05
 ... (omitted values)
1154	34.5
 778    47.1
```
Below is a graphical representation of a calibration curve (made using tap water).

turbcalib

#### Additional notes for calibration accuracy and repeatability

- For each new turbidity being calibrated, it is always recommended to do an average of the recorded values. 
- Ensure that the probe (emitter and receiver) are submersed, and there are no air bubbles between them. Air bubbles influence strongly the readings. 
- Avoid direct sunlight on the turbidity probe during the calibration process. Direct sunlight is likely to alter readings. 
- The ambient light, water temperature and environment conditions (temperature, light and humidity) should be similar to those during the actual tests.
- If **analog#** is obtained automatically, the interval between readings is the one defined in [General settings](https://github.com/Ricardosgeral/relier/blob/master/README.md#general-settings-page) page.

## 7. Data collection
The *acquisition system box* handles the sensors and gets the data from them.  
The location where data will be collected is defined  by the user, and depends
on whether an internet connection is available, and whether a USB drive is plugged in.

### 7.1. No internet connection

Data is only saved locally in the *CSV* format and has two possible ways to go:
  
1. *No USB drive* is plugged in  >>
   Data are saved *only* on the micro SD card, inside folder **/srv/EROSTESTS**. 

2. A *USB is plugged in* >>
   Data are saved *only* on the **USB_root_directory**. 

#### Additional notes

- The name of the *CSV* file is defined by the user, either using:
   + the *touchscreen GUI*, in **General settings** page, or  
   + the *inputs.ini* file, modifying the parameter *filename*.
- Before removing a USB drive or the micro SD card it is ***strongly*** recommended to gently shutdown the *Raspberry Pi*, 
and unplug the power supply.
This will prevent corruption of the micro SD card and of the USB drive, and increase their life span. 
To silently disconnect the server you can either:
   + hold the *red pushbutton* in the back of the *acquisition system box* for more than *3 seconds* (if holden between 1 and 3 seconds, 
   the *Raspberry Pi* will reboot), or 
   + `$ sudo halt` in a *SSH* terminal session.
- If more than one USB drive is plugged in (not recommended !), data will be saved in the *first drive* being found.
- Data in the *CSV* files is ***never deleted*** automatically. If a file with the same name already exists in the USB drive or 
in the micro SD card, data is saved in the file but placed below the last row already there. This means that multiple tests may be collected 
in the same file (not desirable). It is preferable to set each test in an individual file.

### 7.2. Internet connection available (Ethernet or WiFi)

Data collection is also saved locally in *CSV* format. 
That is, if a USB drive is plugged in, data is saved to the USB drive, otherwise, data is saved to the server micro SD card.

However, ***in addition***, it is possible to send data to [Google Sheets](https://www.google.com/sheets/about/), if a valid 
*service_creds.json* file is provided (see instructions in *Software installation > server sofrware*).

#### How to enable 'Google Sheets'
1.  Select that option:
   - In the *touchscreen GUI* > *Settings* > activate the (only) checkbox, or
   - In *inputs.ini* file > ensure that *google_sheets = yes*.
   
2. Provide names for the *Spreadsheet* and for the *Worksheet*:
   - In the *touchscreen GUI* > *Settings*  > *Spreadsheet* (*Worksheet* name = *CSV filename*), or
   - In *inputs.ini* file > Spreadsheet name = *googlesh*, and Worksheet name = *filename*.

3. Provide a valid email, since a link to access the spreadsheet will be shared via email at the start of the test.
   - In the *touchscreen GUI* > *Settings* > Add email, or
   - In *inputs.ini* file > use parameter *share_email*.

#### Additional notes

- If the *Spreadsheet/Worksheet* provided by the user already exists, the data that was in that worksheet will be *deleted* (***Attention***). 
However, when a new Worksheet name is provided in an already existing Spreadsheet, a new sheet is added. 
This means that you can have a single Spreadsheet with different tests organized in different Worksheets (preferable).
- If there is no internet connection, data will not be, of course, sent to Google Sheets, 
even if you select the Google Sheets checkbutton (***Attention***). For debugging please see the 
[troubleshooting](https://github.com/Ricardosgeral/relier#troubleshooting) section. 
- If internet connection is lost during a test, the software will raise an exception and stop recording data to Google Sheets, 
but it will continue to record data locally (USB drive or micro SD card).
- Please be aware that, by choosing the 'Google Sheets' feature, the interval between readings chosen by the user 
will be increased a couple of seconds, due to the time required to request access the Google API. 
If you need an interval between readings smaller than 8 seconds, or you require an always constant interval between readings, 
please disable the 'Google Sheets' feature.

## 8. Achievements and reuse of *Python code*

- Use of the [*ADS1115*](https://www.adafruit.com/product/1085) *Analog to Digital Conversor (ADC)*, to acquire the analog outputs of the pressure sensors and turbidity sensor.
If you want to use another ADC (e.g., the [MCP3008 (10 bits)](https://www.adafruit.com/product/856), 
which is faster but less precise), the Python library will need, of course, to be replaced and the python code should be adapted.
- Use of the [*pigpio library*](http://abyz.me.uk/rpi/pigpio/) to get the readings from the turbine flowmeter (hall-effect sensor), using the function [callback](http://abyz.me.uk/rpi/pigpio/python.html#callback). 
More information [here](https://www.raspberrypi.org/forums/viewtopic.php?t=66445).
- *Use of threading (['thread-based parallelism'](https://docs.python.org/3/library/threading.html)), together with [Event objects](https://docs.python.org/3/library/threading.html#event-objects), in Python 3*. 
Threads are used in this project in three cases: 
   + In the handling of the results from *analog sensors*, for data 'stability'. Threads allow to do a mean over a certain period of time 
   with a shorter delay between samples. This can in some cases improve the data reliability. Thus, 
   the collection of readings from the ADC (ADS1115) is done using a [Thread Class object](https://docs.python.org/3/library/threading.html#thread-objects).   
   + Since *temperature sensors* take some time between reads (about 1 second), 
   the readings of those sensors is done in multi-tasking. 
   This ensures that the interval between readings is the one indicated by the user. 
   Treads are here also used as *Class objects*.
   + Detection of *serial communication* between the server and the Nextion touchscreen. 
   The server needs to check if the touchscreen is pressed, independently of being at the same time doing other tasks. 
   To achieve this it is used *Thread*, alongside with *Event*, both from the threading module. This achievement took me a while to master, and I believe it may be useful to others.
- *Use of Multiprocessing* (['Process-based parallelism'](https://docs.python.org/3/library/multiprocessing.html)). 
Multiprocessing is used to acquire data from the Eletromagnetic flowmeter via serial USB communication. [Value](https://docs.python.org/3/library/multiprocessing.html#multiprocessing.Value) method uses Shared memory to pass values between processes.
- Implementation of a [Ring buffer](https://www.oreilly.com/library/view/python-cookbook/0596001673/ch05s19.html), to avoid overflow of readings coming from the ADC chip.
- *Library for serial communication with the Nextion device in Python 3* (TX-RX, UART protocol). 
Unfortunately, until the day I'm writing this, a Python library to use Nextion touchscreen was not available.
There is a good library developed for Arduino, but I did not want to mix Python and *C* code. 
So, I've developed my own Nextion Library for Python 3 (which took me a while to achieve !).
This library is relatively simple to use, and has margin for improvement. 
You just need to look at the [*py3nextion_lib.py*](https://github.com/Ricardosgeral/relier/blob/master/py3nextion_lib.py),
and use it alongside with [*nextionApp.py*](https://github.com/Ricardosgeral/relier/blob/master/nextionApp.py) 
that has all the components (to be accessed by the server) defined in the Nextion Editor. 
Function *detect_touch()* in [main.py](https://github.com/Ricardosgeral/relier/blob/master/main.py)
is responsible for the continuous listening of the Nextion return bits, and the execution of for the following actions.
Of course, you need to know how to use the Nextion commands.
For that, see the [*instructions set*](https://nextion.itead.cc/resources/documents/instruction-set/).
- Use of the library [*pygsheets*](https://github.com/nithinmurali/pygsheets), alongside with 
library [*pandas*](https://pandas.pydata.org/index.html), to collect data from multiple sensors and send them to Google Sheets.  
- Use the library [*CSV*](https://docs.python.org/3.6/library/csv.html) to write the data (as dictionary) in rows.
- Use of the library [*configparser*](https://docs.python.org/3/library/configparser.html) to have a *.ini* file 
with the inputs.
- Use of the library [pyserial](https://pythonhosted.org/pyserial/), to read from the TX/RX (communication with the Nextion) and USB serial ports (communication with the Eletromagnetic flowmeter).
- Automatic detection when USB drives are plugged-in (mounted) or removed (unmounted).
 This also implies writing two rules in file *99-local.rules*.
- Combined Restart / Shutdown Button for Raspberry Pi 
(using a [*systemd service*](https://wiki.debian.org/systemd)) more info see [shutdown_button](https://github.com/scruss/shutdown_button): 
   + *Reboot*: hold the button more than half second but less than 3 seconds. The LED blinks with blue color and then the RPi reboots. 
   + *Shutdown*: hold the button more than 3 seconds. The LED blinks with red color and then the RPi shutdowns.
   Note, that the Raspberry Pi is still powered. 
 You still need to unplug the micro USB cable, to power off the server. 
 To restart the server after a shutdown, just power up the server again.
- Detection of the local *IP address* of the server (if connected to the internet).
- Start a python script right after start up or reboot of the server (*Raspberry Pi*), 
using [*crontab*](https://debian-administration.org/article/56/Command_scheduling_with_cron).
- Enable IC2 and 1-wire GPIO in file */boot/config.txt*.
- Enable pins 14(TX) and 15(RX) to use UART serial connection (where Nextion device is connected).  

## 9. Troubleshooting
 
- The following warning is expected: *'grep: /dev/fd/63: No such file or directory'* at the end of 
`$ sudo ./raspbian-post-install.sh`. Ignore it.
- Don't forget to obtain and replace the content of the file [*service_creds.json*](https://github.com/Ricardosgeral/relier/blob/master/service_creds.json), 
as indicated [above](https://github.com/Ricardosgeral/relier/blob/master/README.md#server-software-raspberry-pi), 
or the " Export to Google Sheets" feature will not work!
- The inspection of the **cronlog** file (`$ sudo nano /home/pi/relier/logs/cronlog`) may be helpful for detecting 
any eventual bugs during the software installation process, or during start up of the server, for example, 
to check if the Google credentials are correct!.
- *'Problem: Google signed Credentials'*. In this case, confirm that you have an internet connection,
and that you followed all 6 steps in installation of the server software. Don't forget to enable the 'Drive API' (step 4).
- If the Nextion touchscreen is not functioning properly or not working at all:
  + first, see the connections, in particular check that: RX (server) <-> TX (screen), and TX (server) <-> RX (screen); 
  + second, confirm that the baudrate is correct. By default nextion comes with 9600, but in program it is defined as 38400. This means that in first time
  the nextion needs to be set to that baud rate using file *pynextion_lib.py*.
  + third, ensure that *serial* is disconnected: `$ sudo raspi-config` > *5* > *P6 Serial* > *No*;
  + last, doing `$ ls -l /dev | grep serial` you should see *serial 0 >> ttyAMA0* (pins 14/15 in UART) and 
  *serial 1 >> ttyS0* (bluetooth in miniuart). By default UART is attributed to Bluetooth and miniuart to pins 14/15 (which has limitations). 
  That's why they are changed during the execution of 
  [*raspbian-post-install.sh*](https://github.com/Ricardosgeral/relier/blob/master/bash/raspbian-post-install.sh).
- To check if the *Analog-to-Digital Converter* (ADC - ADS1115 chip) and BME280 are properly connected via I2C, you can do 
*`$ sudo i2cdetect -y 1`*. 
 You should see a matrix with number ***48*** (ADS 1x15) and number ***76*** (BME280). 
 Otherwise, something is not connected correctly, or I2C protocol has not been enabled 
 (again, the bash file [*raspbian-post-install.sh*](https://github.com/Ricardosgeral/relier/blob/master/bash/raspbian-post-install.sh) should have done that !).
- If you want to check if the Linux service units running on reboot/shutdown are active, check their status.
 ```
 $ sudo systemctl status rcshut
 $ sudo systemctl status shutdown_button
 ```   
   `Ctr + D ` to leave the terminal.
- If you, by any reason (e.g., for debugging), need to stop all the python scripts that are running from startup of the server, 
open a terminal and execute:
 ```
 $ sudo pkill -9 python
 ```

## 10.  About the author and the *relier* project
I'm a Civil Engineer, with a [master degree](https://www.researchgate.net/publication/273715929_Enquadramento_das_analises_de_riscos_em_Geotecnia) 
in risk analysis in Geotechnical Engineering, and a [PhD](https://www.researchgate.net/publication/265396445_Experimental_investigation_on_limitation_of_the_progression_of_internal_erosion_in_zoned_dams?_sg=TYpuvUDlOEmsy1nkmycUNZZQmLHo34eFR1un5kQBsel1Ih6m8itcptNphw4q33ZLbFPsnKm5uX3PfaJmW1fljV7_goXnxDN4Ne4RwewR.OOCKioxBNPJoOd0B8BiFk4-Dqk849OZdMI_lxDR_IRduPQ88ovShdBBoVm34ZNhMTA_UT3M8PANv1KdYr7rMXg) 
on internal erosion in embankment dams.
 
Carrying out the [laboratory tests on internal erosion in soils](https://www.researchgate.net/publication/317742058_Limitation_of_the_progression_of_internal_erosion_in_zoned_dams), 
developed in my PhD, 
requires to simultaneously collect different types of measurements (water pressures, flow rate, temperature, turbidity, ...).
The measurements had to be registered by hand, in regular intervals, by two operators!! 
Such manual process is tedious and prone to errors.

So, I've decided to invest time developing a 'low budget' acquisition system (hardware and software) that could 
collect data automatically from multiple analog and digital output sensors. 
*relier* born this way!

Please note that I'm not an expert in informatics, in computing, nor in electronics.
I define myself as an enthusiastic self learner. 
All shown here was developed from my own research, mainly on forums, Github and other websites.
Thus, it is possible that some things (code, connections, methods...) could be optimized, or done in a different or a better way. 
Yet, ***relier*** *acquisition system* performs as intended.
You can report bugs, suggest enhancements, or even fork the project on [Github](https://github.com/Ricardosgeral/relier). 
All contributions are welcome.

## 11. Acknowledgements
My thanks to *António Timóteo* (LNEC-DG technician) for his work on cutting the openings in the acquisition aluminium box. 
Also, my thanks to *João Paixão* (LNEC-CIC technician) for soldering the smaller and more difficult parts 
(cup terminals of the mini aviator plugs and the pines in the ADC and of the level shifter).

## 12. License
Copyright (c) 2019 Ricardo Correia dos Santos

See the [license conditions](https://github.com/Ricardosgeral/relier/blob/master/LICENSE).

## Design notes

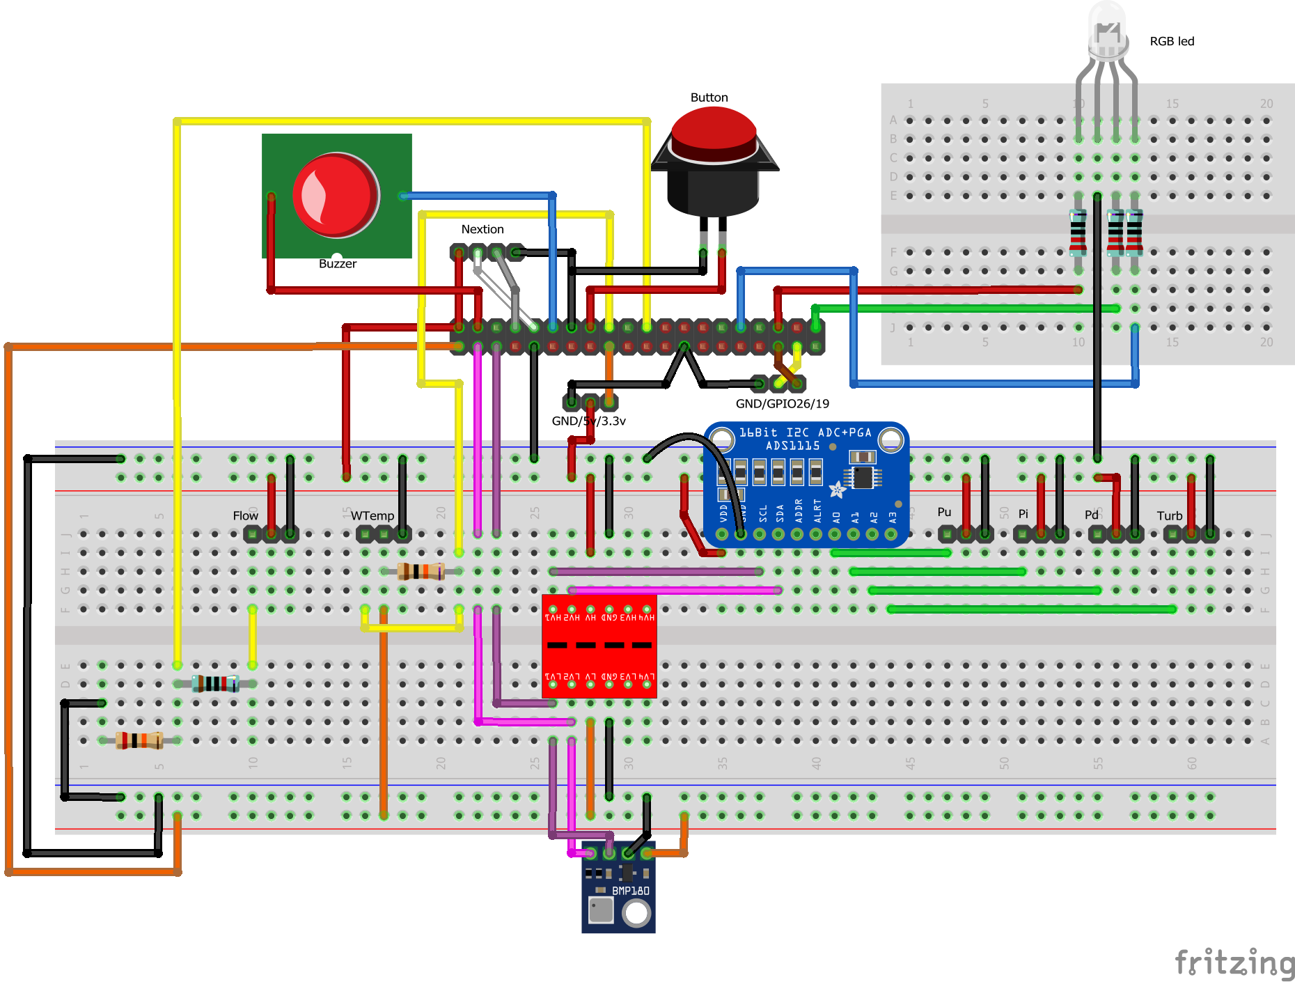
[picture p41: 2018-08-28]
Fritzing/v3.0-hat/images/relierv3_hat_bb.png

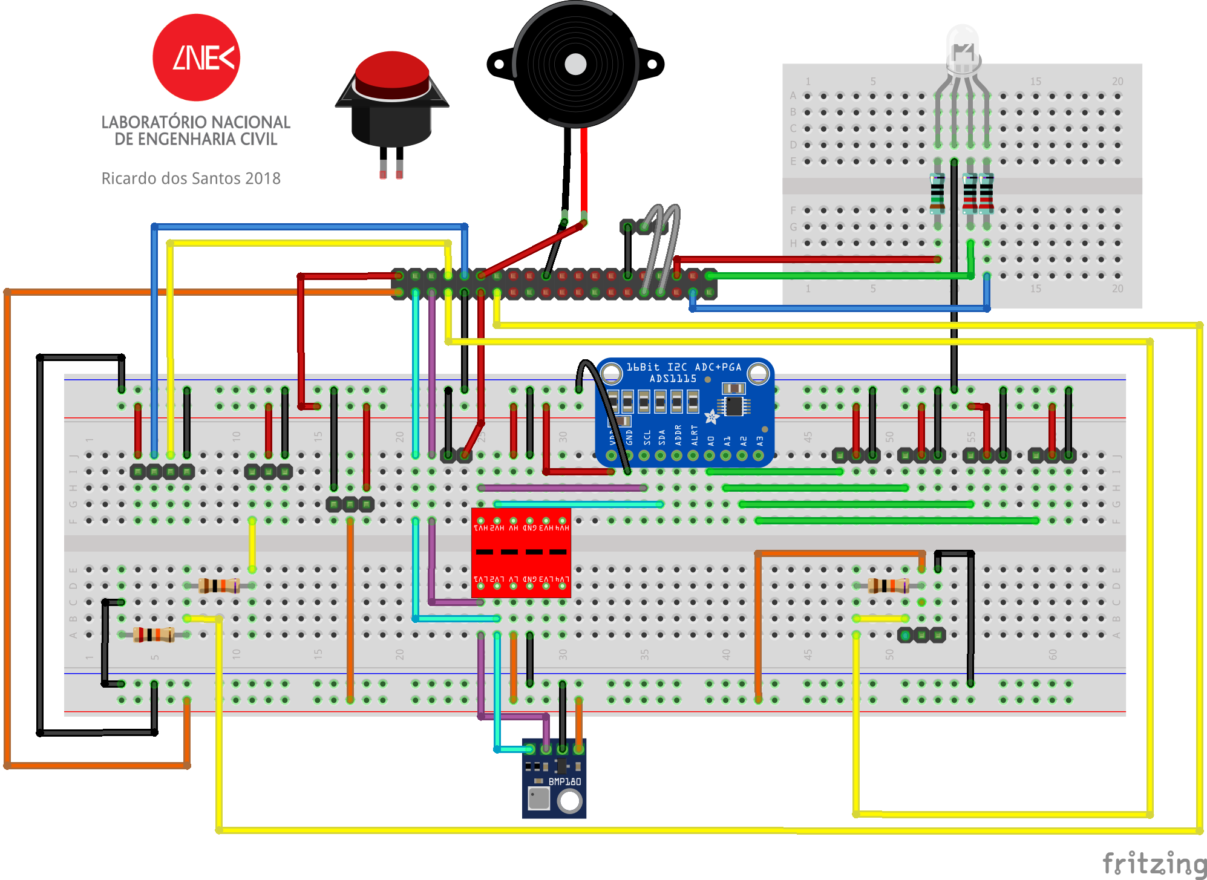
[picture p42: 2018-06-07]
Fritzing/v2/images/relierv2_bb.png

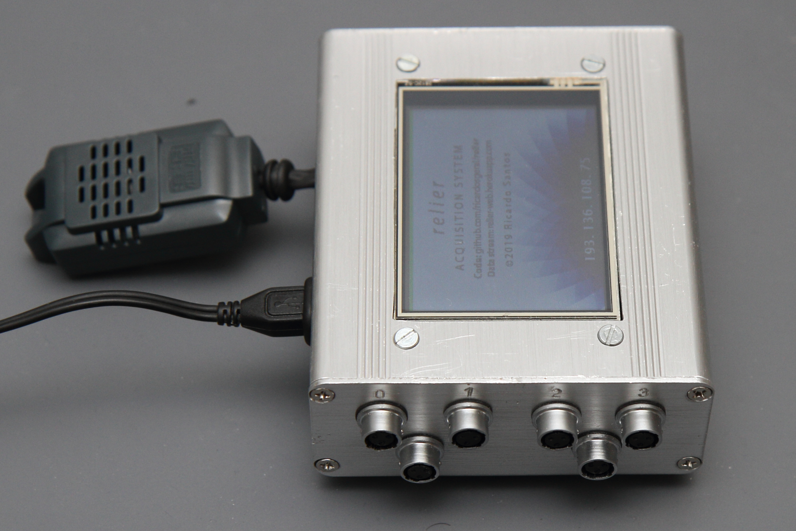
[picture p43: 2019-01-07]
Media/images/geral/2019-01-07_relierv3_035.JPG

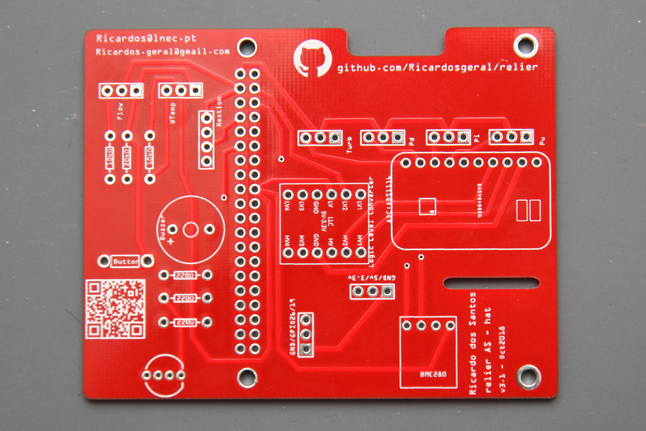
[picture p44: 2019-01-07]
Media/images/geral/2019-01-07_relierv3_008.JPG

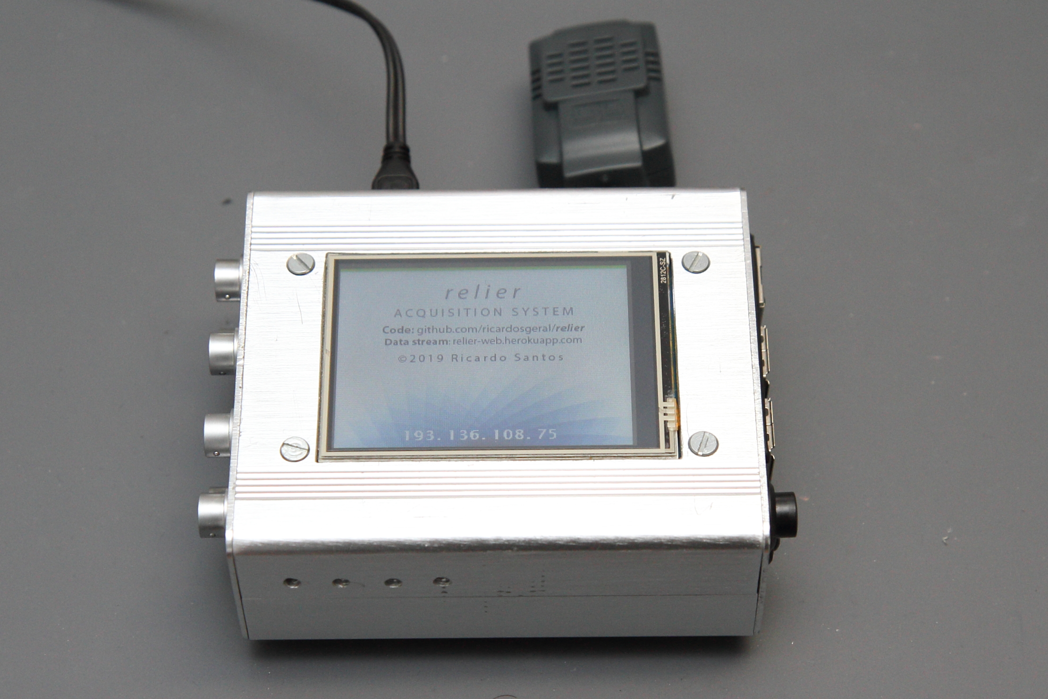
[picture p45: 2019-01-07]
Media/images/geral/2019-01-07_relierv3_039.JPG

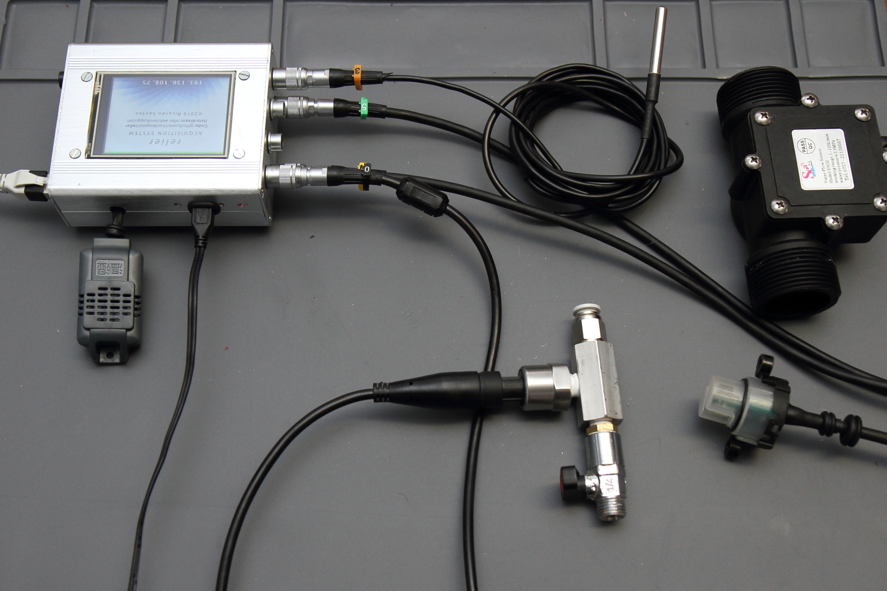
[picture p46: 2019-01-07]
Media/images/geral/2019-01-07_relierv3_024.JPG

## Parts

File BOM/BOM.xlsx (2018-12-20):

Qt | price/un* | Total | Description | Note
1 | 35 | 35 | [Raspberry pi 3B](https://www.raspberrypi.org/products/#buy-now-modal) | Server
1 | 16.2 | 16.2 | [Nextion HMI touch display 2.8"](https://www.itead.cc/nextion-nx3224t028-1933.html) | Graphical User Interface (GUI)
1 | 6.2 | 6.2 | [Aluminium enclosure box (88x38x100mm)](https://www.aliexpress.com/item/Free-shipping88-38-100mm-width-x-high-x-length-aluminum-extrusion-box-profile-enclosure-for-PCB/32800855972.html | Enclosure of the raspberry, the hat and the custom PCB
2 | 10 | 20 | Micro SD card (>8GB) | One for the raspberry pi and another for the Nextion display (during instalation)
1 | 8 | 8 | [Raspberry Pi Power Supply](https://www.raspberrypi.org/products/raspberry-pi-universal-power-supply) | Power of the raspberry pi and the sensors
1 | 1 | 1 | [Raspberry pi Hat - Custom PBC](http://www.pcbway.com/project/shareproject/Relier_Acquisition_system___for_Rasoberry_pi3_b_.html): | Interlinks server, touchscreen and the sensors
1 | 1.4 | 1.4 | - [16 Bit I2C ADS1115 Module ADC 4 channel with Pro Gain Amplifier](https://www.aliexpress.com/item/16-Bit-I2C-ADS1115-Module-ADC-4-channel-with-Pro-Gain-Amplifier-RPi-1PCS/32817162654.html | Analog to Digital Conversor for analog sensors
1 | 0.3 | 0.3 | - [Logic Level Shifter Bi-Directional 5V to 3.3V](https://www.aliexpress.com/item/5PCS-Logic-Level-Shifter-Bi-Directional-For-Arduino-5V-to-3-3V-Four-Way-Two-Way/32827270848.html | Required for stability, since ADS1115 requires 5V and raspberry I2C pins use 3.3V
6 | 3.8 | 22.8 | - [8mm Male & Female Connector miniature Aviation Plug M8 Circular Socket+Plug](https://www.aliexpress.com/item/1PCS-AP049-YC8-2-3-4-5-6-7Pin-8mm-Male-Female-Connector-miniature-Aviation-Plug/32845374887.html | Connection of the sensors to the acquisition box
6 | 0.2 | 1.2 | - [XH2.54 3-Pins connectors Male for PCB - Header+Housing+Terminal](https://www.aliexpress.com/item/XH2-54-2P-3P-4P-5P-6P-7P-8P-9P-10P-11P-12P-13P-14P-15P/32793262315.html | Connection of miniature aviation plugs to the custom PCB
2 | 0.2 | 0.4 | - [XH2.54 4-Pins connectors Male for PCB - Header+Housing+Terminal](https://www.aliexpress.com/item/XH2-54-2P-3P-4P-5P-6P-7P-8P-9P-10P-11P-12P-13P-14P-15P/32793262315.html | Connection of Nextion display and BME280 sensor to the custom PCB
1 | 0.9 | 0.9 | - [PC104 2.54mm Pitch 2x20 Pin 40 Pin Female Double Row Long Pin Header Strip](https://www.aliexpress.com/item/2-Pcs-PC104-2-54mm-Pitch-2x20-Pin-40-Pin-Female-Double-Row-Long-Pin-Header/32805691836.html) | Connection between Raspberry GPIO and custom PCB
1 | 0.2 | 0.2 | - [Momentary pushbutton switch 3A Reset Button](https://www.aliexpress.com/item/10pcs-Momentary-Push-Button-Switch-12mm-Momentary-pushbutton-switches-3A-125VAC-1-5A-250VAC-Reset-Button/32802331189.html | Safe restart or shutdown of the raspberry
1 | 0.1 | 0.1 | - 5 mm RGB LED | Indicative multicolor LED
1 | 0.1 | 0.1 | - Active Buzzer Alarm 5 V | Indication of end of test
3 | 0.02 | 0.06 | - 220 Ω carbon film resistor | Protection of the RGB LED
2 | 0.02 | 0.04 | - 10 kΩ carbon film resistor | 1 for voltage divider (turbine flowmeter) and other for water temperature sensor
1 | 0.02 | 0.02 | - 20 kΩ carbon film resistor | Voltage divider (turbine flowmeter)
3 | 0.01 | 0.03 | - 0805 SMD 1/4W resistor 1MΩ | Pull up resistors to know when there is no sensors connected
6 | 0.1 | 0.6 | - 5 cm cable with 3 wires [< 1 €] | Connection between mini aviator plugs and XH2.54 connectors
1 | 0.1 | 0.1 | - 8 cm cable with 4 wires | Connection between BME280 and the custom PCB
 |  | 114.65
SENSORS
Qt | price/un | Total | Description | Note
3 | 13 | 39 | [Analog Pressure Transducer Transmitter Sensor, 0-5psi 0.5-5V](https://www.aliexpress.com/item/1Pc-Pressure-Transducer-Sender-Stainless-Steel-for-Oil-Fuel-Air-Water-5psi-CSL2017/32814346612.html | Measures water pressure at different levels (piezometers)
1 | 9 | 9 | [Analog Turbidity Sensor, 5V 40mA](https://www.aliexpress.com/item/DFRobot-Gravity-Analog-Digital-Turbidity-Sensor-5V-40mA-DC-support-both-signal-output-compatible-with-arduino/32595773560.html | Measures the turbidity of effluent water
1 | 13 | 13 | [Digital Turbine Flow Sensor, G5/4, 1.25", DN32, 1~120L/min](https://www.aliexpress.com/item/DN32-Water-Flow-Meter-Sensor-Switch-G5-4-Thread-Port-Industrial-Flowmeter/32567971320.html | Measures the water flow (it is also possible to use a eletromagnetic type flowmeter)
1 | 1 | 1 | [Waterproof DS18B20 digital Temperature Sensor](https://www.aliexpress.com/snapshot/0.html?orderId=505161631680030&productId=32675444739) | Measures the water temperature
1 | 3 | 3 | [BME280 Digital Sensor, Humidity, Temperature and Barometric Pressure Sensor](https://www.aliexpress.com/item/3In1-BME280-GY-BME280-Digital-Sensor-SPI-I2C-Humidity-Temperature-and-Barometric-Pressure-Sensor-Module-1/32659765502.html | Measures the atmosferic temperature, humidity and pressure
 |  | 65
 |  | 179.65 |  |  | V | bar | mV | mbar | mmH2O
 |  |  |  |  | 1.2 | 0.05994 | 1200 | 59.94 | 611.2178981
 |  |  |  |  | 0.625 | 0.010375 | 625 | 10.375 | 105.7955571

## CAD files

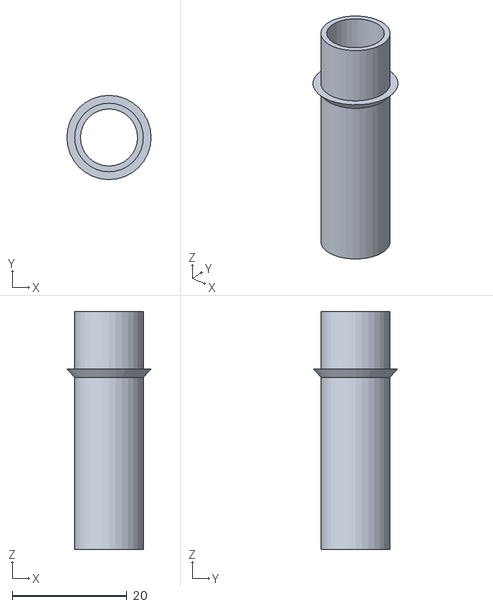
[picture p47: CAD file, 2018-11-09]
3Dprint/turbidity_v3_part3.stl
14.7 x 14.7 x 41.5

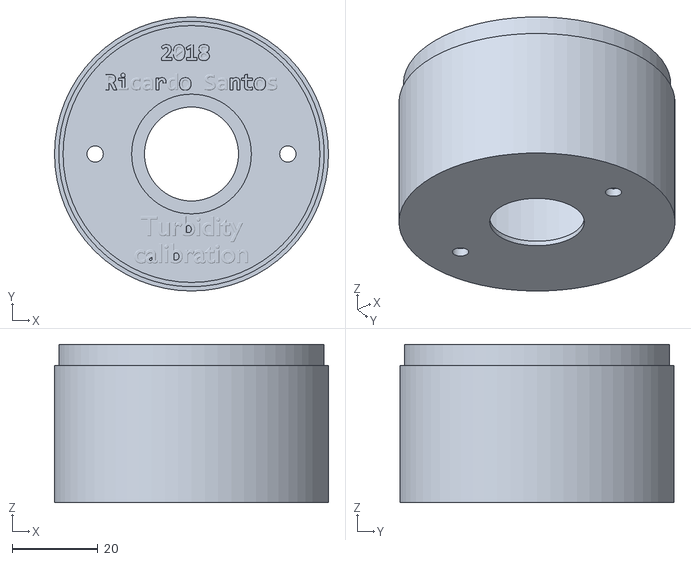
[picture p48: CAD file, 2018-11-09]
3Dprint/turbidity_v3_part1.stl
64.0 x 64.0 x 37.0

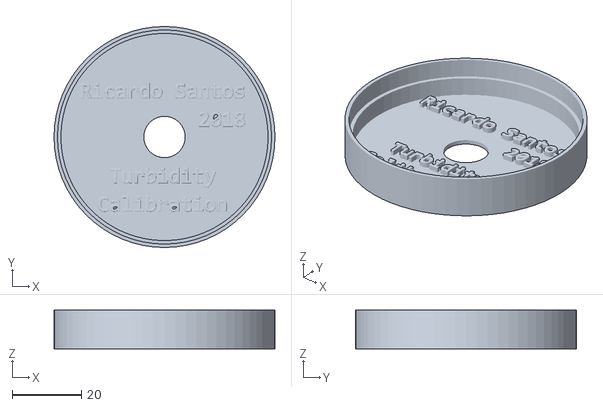
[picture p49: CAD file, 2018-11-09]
3Dprint/turbidity_v3_part2.stl
64.0 x 64.0 x 11.2

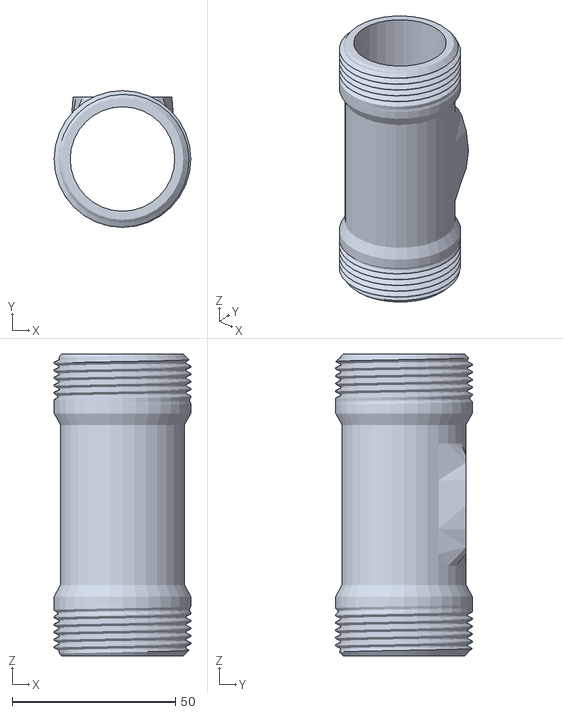
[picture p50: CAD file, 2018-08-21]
3Dprint/TEST_TURB_v1.stl
41.9 x 41.9 x 92.5

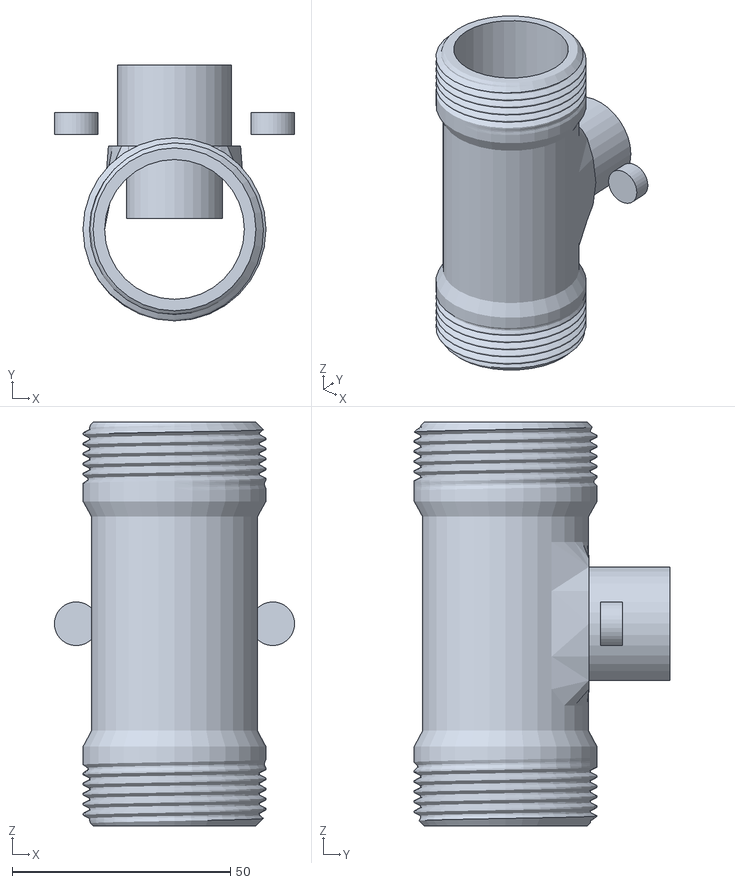
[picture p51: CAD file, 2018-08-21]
3Dprint/TEST_TURB.stl
55.0 x 58.6 x 92.5

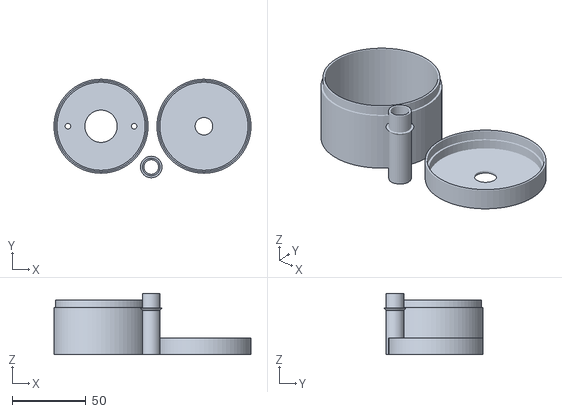
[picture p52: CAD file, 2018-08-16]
3Dprint/turbidity_v3.stl
134.0 x 67.1 x 41.5

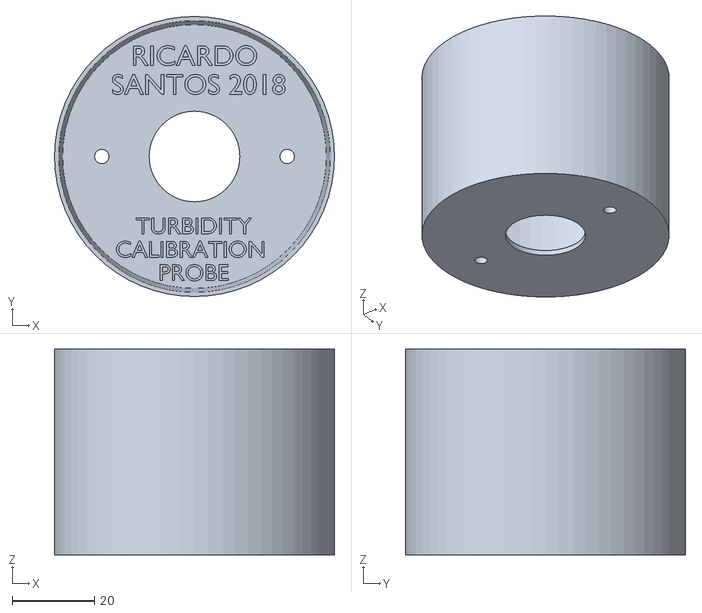
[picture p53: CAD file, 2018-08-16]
3Dprint/turbidity_v2_1.stl
68.0 x 68.0 x 50.0

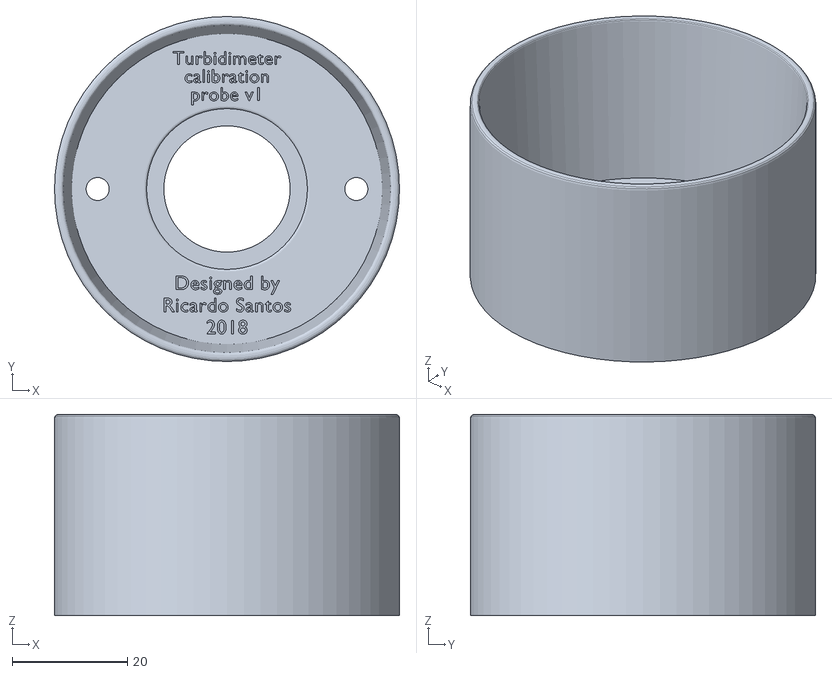
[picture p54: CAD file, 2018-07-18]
3Dprint/turbidity_v1.stl
60.0 x 60.0 x 35.0

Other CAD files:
box/Enclosure box_openings.dwg
3Dprint/TEST_TURB_v2.stl

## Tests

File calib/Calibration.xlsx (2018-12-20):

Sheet: turbidity_ODL_#40
water volume used: | 400 | ml
soil tested | cumulative | measured
grams | grams | analog number | grams/liter
0.1 | 0.1 | 24971 | 0.25
0.1 | 0.2 | 23000 | 0.5
0.1 | 0.3 | 21030 | 0.75
0.1 | 0.4 | 18900 | 1
0.2 | 0.6 | 17102 | 1.5
0.2 | 0.8 | 15737.8 | 2
0.2 | 1 | 14458.83333 | 2.5
0.4 | 1.4 | 11934.57143 | 3.5
0.4 | 1.8 | 10092 | 4.5
0.4 | 2.2 | 8060.166667 | 5.5
0.4 | 2.6 | 6636 | 6.5
0.4 | 3 | 5493 | 7.5
0.5 | 3.5 | 4071.5 | 8.75
0.5 | 4 | 3425.666667 | 10
0.5 | 4.5 | 2607.714286 | 11.25
0.5 | 5 | 2105 | 12.5
0.5 | 5.5 | 1548.8 | 13.75
0.5 | 6 | 1334 | 15
1 | 7 | 895 | 17.5
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

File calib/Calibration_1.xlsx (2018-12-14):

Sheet: turbidity_ODL_#40
water volume used: | 400 | ml
soil tested | cumulative | measured
grams | grams | analog number | grams/liter
0.1 | 0.1 | 24971 | 0.25
0.1 | 0.2 | 23000 | 0.5
0.1 | 0.3 | 21030 | 0.75
0.1 | 0.4 | 18900 | 1
0.2 | 0.6 | 17102 | 1.5
0.2 | 0.8 | 15737.8 | 2
0.2 | 1 | 14458.83333 | 2.5
0.4 | 1.4 | 11934.57143 | 3.5
0.4 | 1.8 | 10092 | 4.5
0.4 | 2.2 | 8060.166667 | 5.5
0.4 | 2.6 | 6636 | 6.5
0.4 | 3 | 5493 | 7.5
0.5 | 3.5 | 4071.5 | 8.75
0.5 | 4 | 3425.666667 | 10
0.5 | 4.5 | 2607.714286 | 11.25
0.5 | 5 | 2105 | 12.5
0.5 | 5.5 | 1548.8 | 13.75
0.5 | 6 | 1334 | 15
1 | 7 | 895 | 17.5
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

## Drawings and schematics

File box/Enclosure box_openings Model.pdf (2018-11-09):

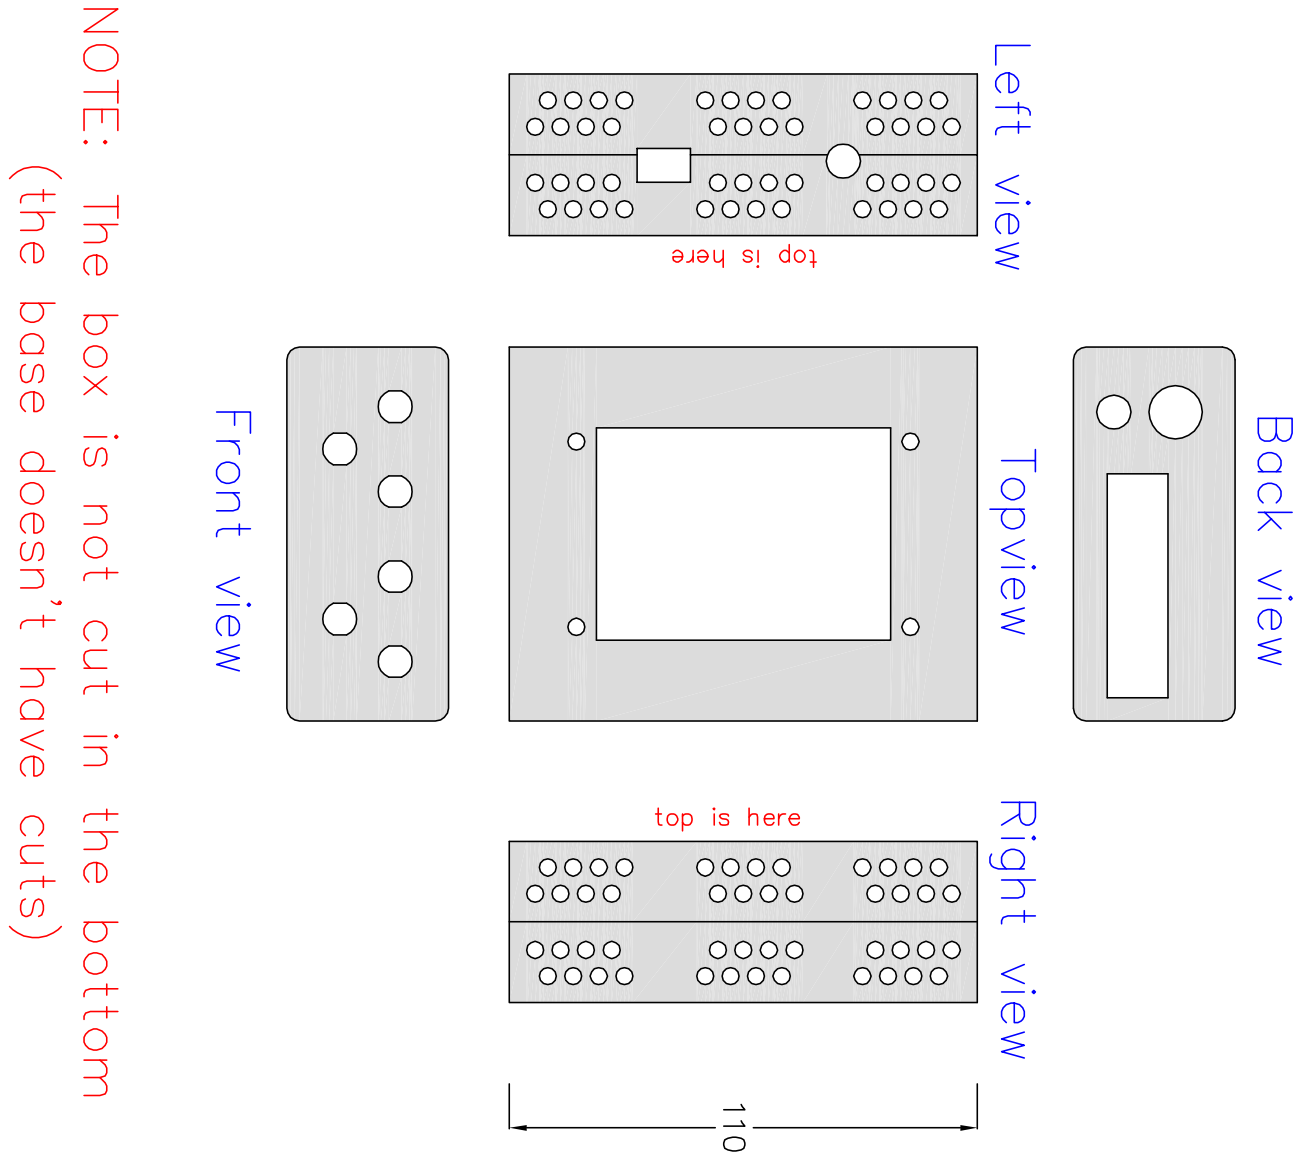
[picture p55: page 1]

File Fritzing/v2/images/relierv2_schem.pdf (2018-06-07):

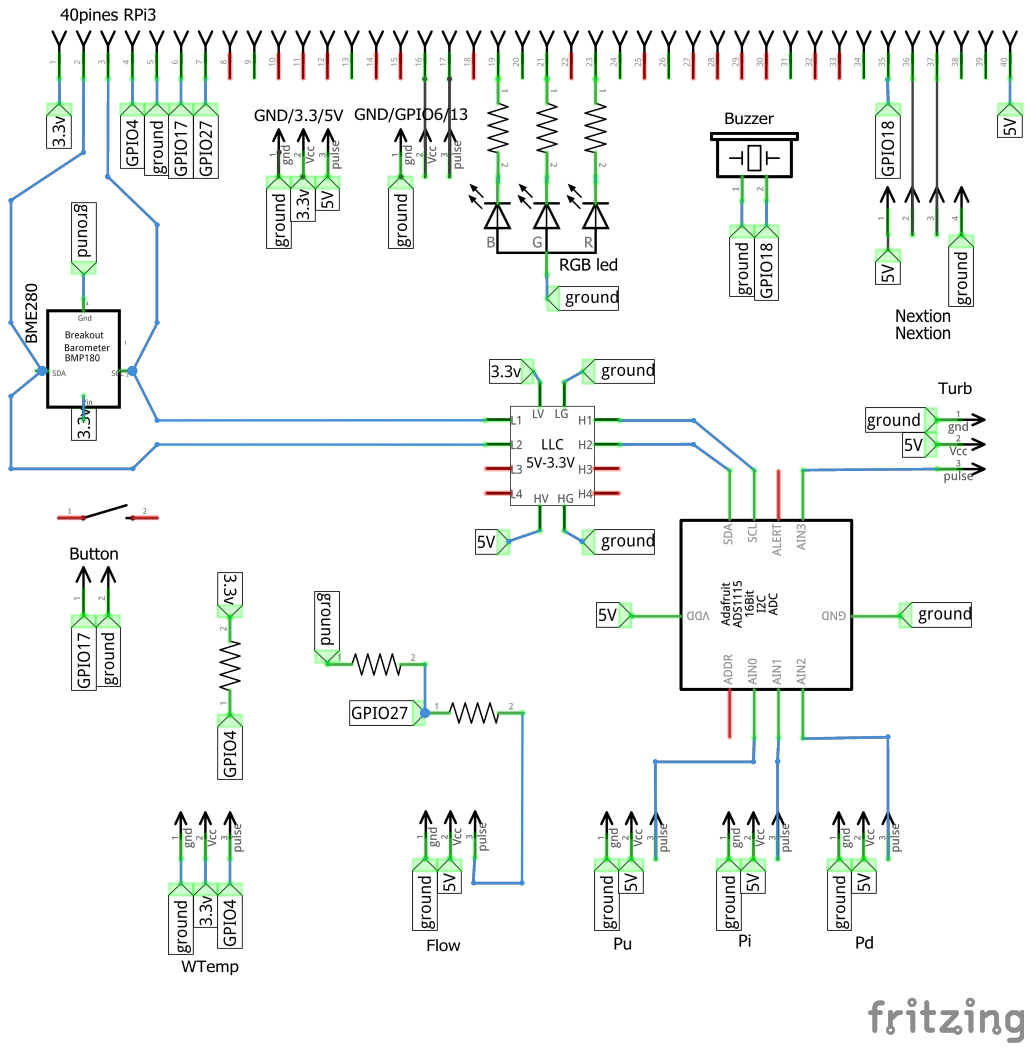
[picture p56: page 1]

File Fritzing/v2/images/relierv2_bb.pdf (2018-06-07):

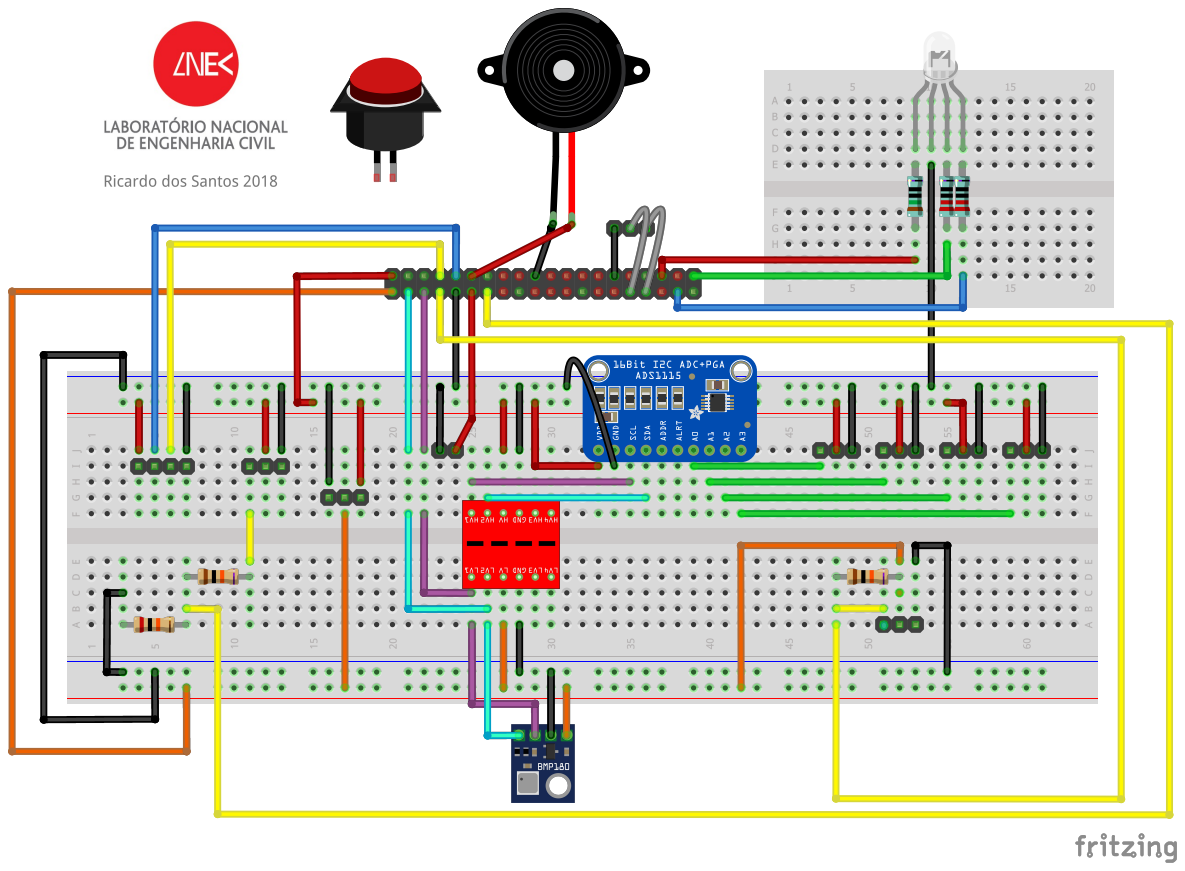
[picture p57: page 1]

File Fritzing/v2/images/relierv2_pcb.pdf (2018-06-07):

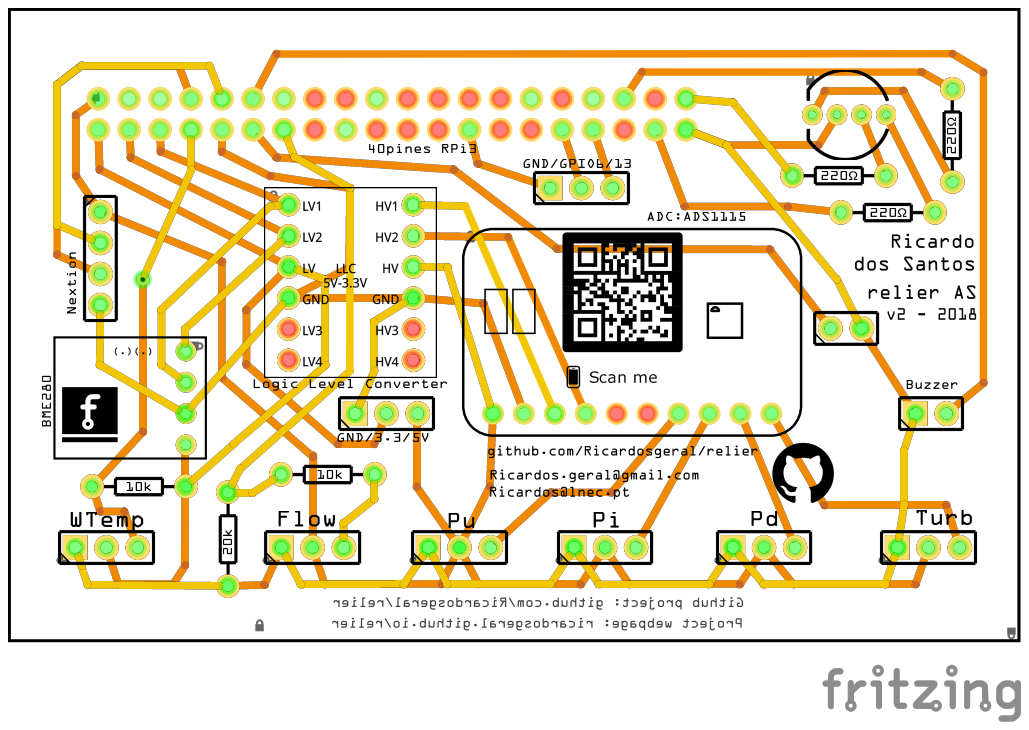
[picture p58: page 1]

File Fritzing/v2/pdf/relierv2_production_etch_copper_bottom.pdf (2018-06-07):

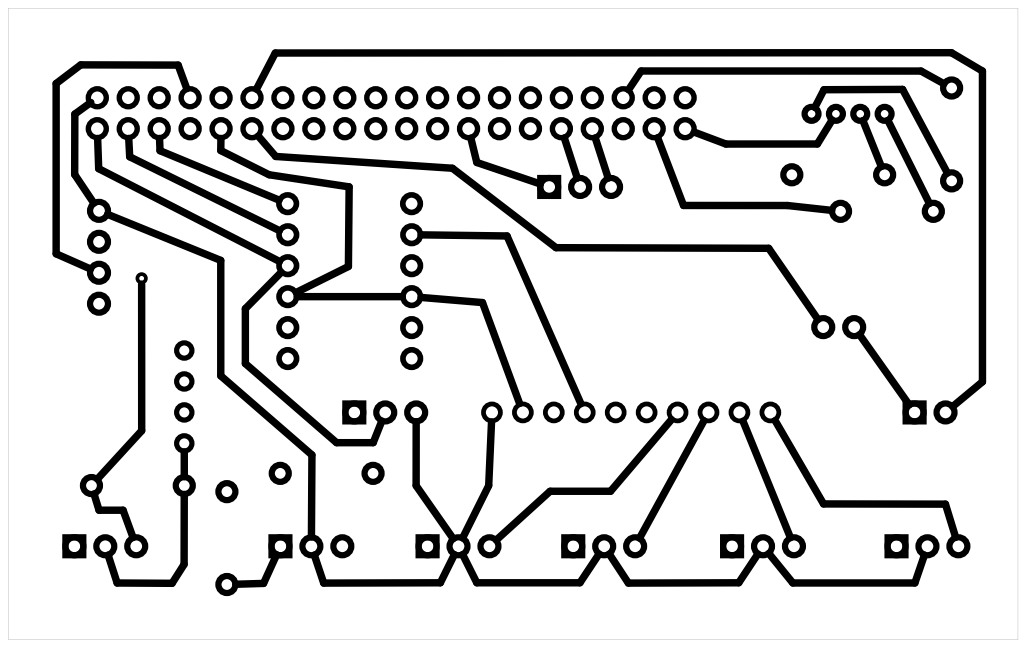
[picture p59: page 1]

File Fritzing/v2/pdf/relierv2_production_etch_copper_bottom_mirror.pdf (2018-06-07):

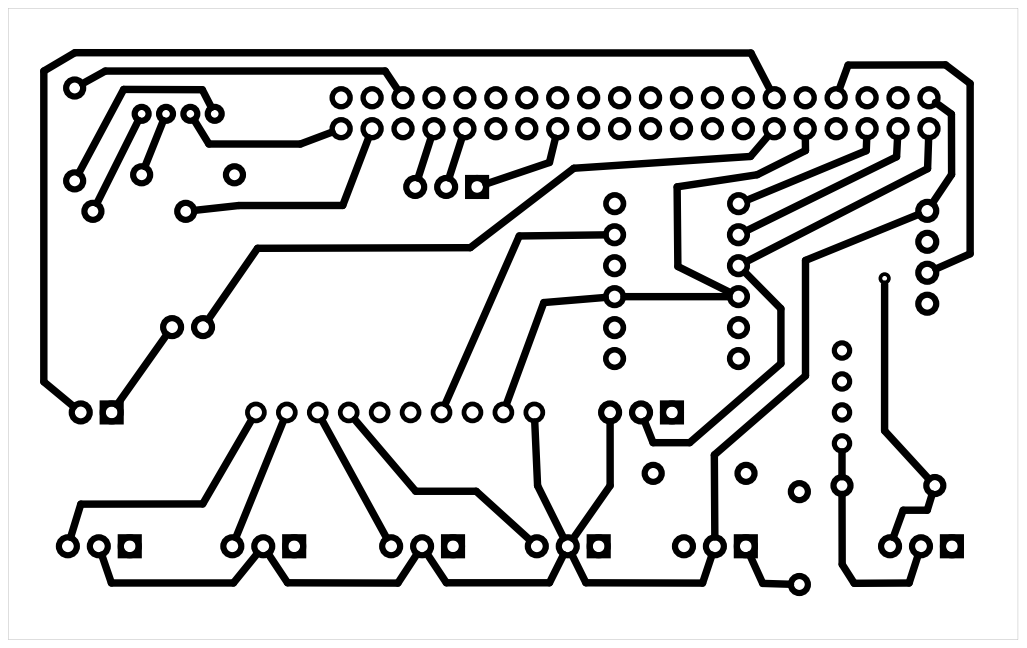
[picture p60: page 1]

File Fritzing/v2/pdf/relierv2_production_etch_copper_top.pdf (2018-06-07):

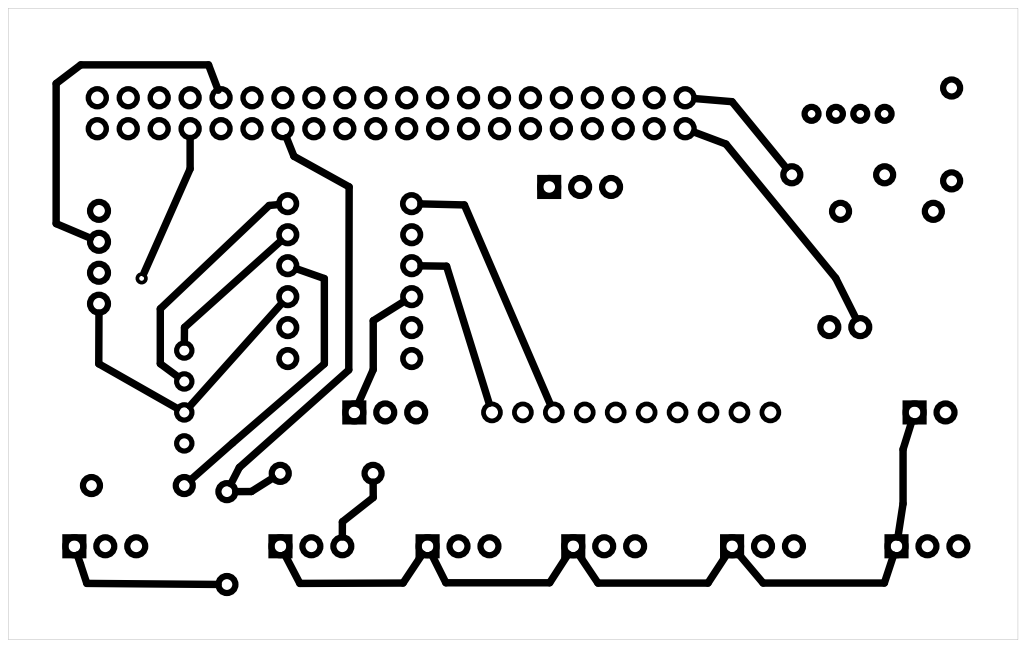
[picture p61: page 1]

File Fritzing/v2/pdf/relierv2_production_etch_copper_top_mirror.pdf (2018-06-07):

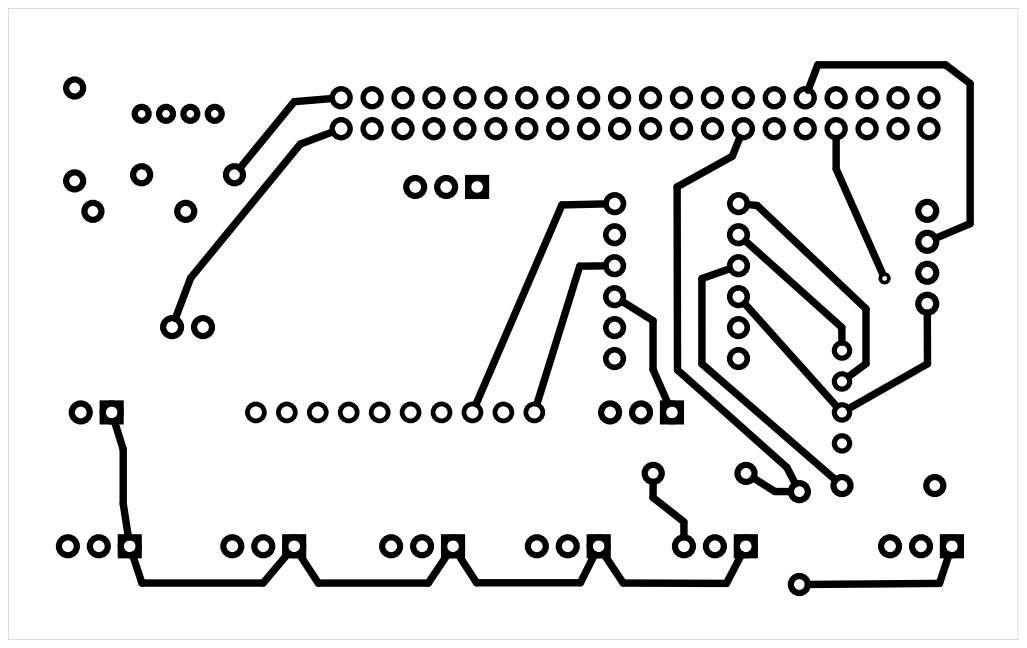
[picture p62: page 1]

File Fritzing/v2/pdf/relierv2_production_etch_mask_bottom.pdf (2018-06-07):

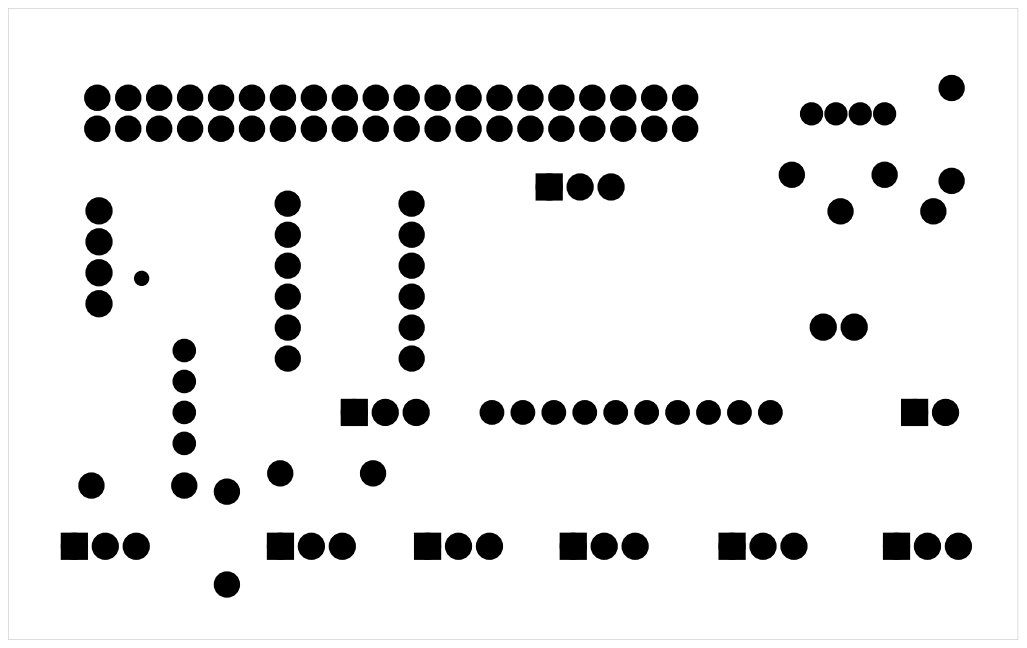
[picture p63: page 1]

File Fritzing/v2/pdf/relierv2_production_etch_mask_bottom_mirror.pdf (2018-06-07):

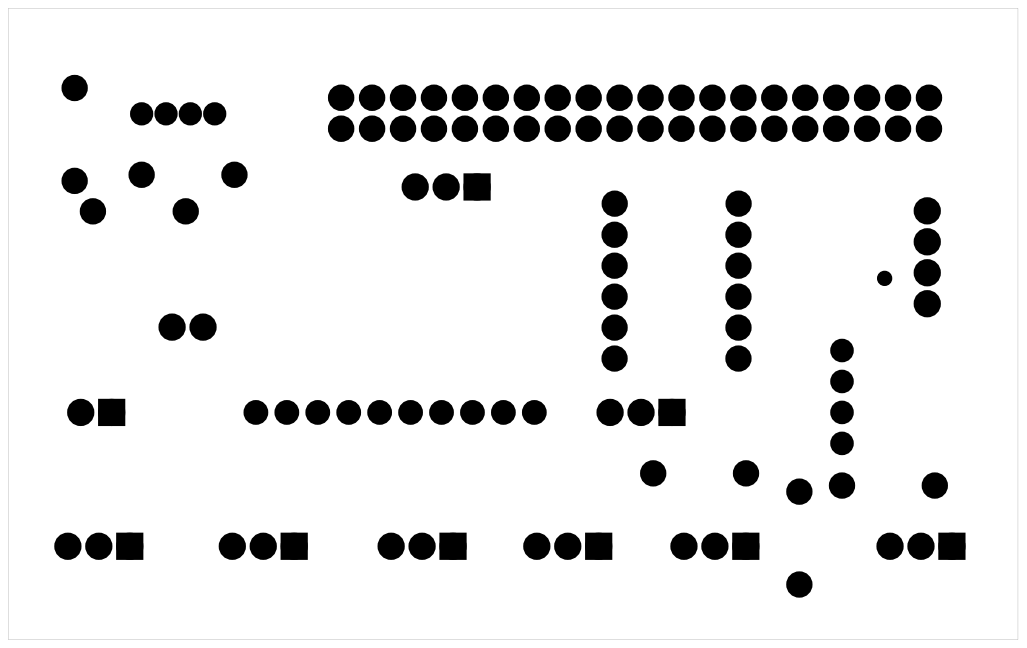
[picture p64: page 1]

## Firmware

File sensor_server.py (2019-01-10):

#! /usr/bin/python3
# -*- coding: utf-8 -*-
#Ricardos.geral@gmail.com

"""Server that reads values from different sensors for lab test.

This script is a server that is supposed to run on a RPi with the
adequate sensors hooked to it via GPIO.
It reads the value of the sensors then store them on disk or on
the usb drive if one is plugged, it also always export local data on
the usb drive if there are local data.
The measurements are always stored in csv format in "/srv/sensors/" or directly at the root of the usb.

The sensors are:
    BME280 GY-BME280 : ambient temperature humidity and barometric pressure
    DS18B20 : water temperature: Direct waterproof DS18B20 digital temperature sensor (probe)
    Turbidity Sensor (dishwasher) : turbidity of water
                                    DFRobot Gravity Analog/Digital Turbidity Sensor, 5V 40mA DC
    3 pressure sensors : 0-5psi 5V Pressure Transducer Transmitter Sensor or Sender
    flow sensor : flowrate and total liters. It is possible to choose between two different types of flowmeters:
                1- Eletro-magnetic flowmeter (Danfoss Mag) - connected via serial port
                2- 1.25" DN32 1~120L/min water Plastic Hall Turbine flow sensor industry meter (Sea brand)

It also records the time and date of the measure.

"""

# Libraries required
from time import sleep
from analogsensor_thread_buf import AnalogSensor, GAIN, DATA_RATE
from digitalSen_thread import D_Temp
import FlowMAG  # for the eletromagnetic flow meter from Danfoss
import multiprocessing  # the reading of FLOWMAG is placed in a different process
from datetime import datetime
import turbidity_calibration  # to get data from a txt with calibrated turbidity sensor
import pigpio   # needs to be installed for callback https://www.raspberrypi.org/forums/viewtopic.php?t=66445
import Adafruit_ADS1x15  # Analogic digital conversor ADS 15 bit 2^15-1=32767 (needs to be installed using pip3)
adc = Adafruit_ADS1x15.ADS1115(address=0x48, busnum=1)  # address of ADC See in -- sudo i2cdetect -y 1

# Constants
PATH_TO_MEDIA = '/media'  # to save in USB flash drive placed in raspberry pi

#Channel numbers in ads1115 analog to digital converter DAC
PRESSUP_ch = 0     # piezometric pressure in upstream chamber
PRESSINT_ch = 1    # piezometric pressure in interface
PRESSDW_ch = 2     # piezometric pressure in downstream chamber
TURB_ch = 3        # turbidity of outlet water

# Relation Gain voltages for ADS1115 chip:
#  - 2/3 = +/-6.144V
#  -   1 = +/-4.096V
#  -   2 = +/-2.048V
#  -   4 = +/-1.024V
#  -   8 = +/-0.512V
#  -  16 = +/-0.256V

if GAIN == 1:
    max_VOLT = 4.096
elif GAIN == 2:
    max_VOLT = 2.048
elif GAIN == 4:
    max_VOLT = 1.024
elif GAIN == 4:
    max_VOLT = 0.512
elif GAIN == 4:
    max_VOLT = 0.256
else: # GAIN == 2/3
    max_VOLT = 6.144

#For the flowmeter
FLOW_ch = 25       #GPIO25 in raspberry pi3
pi = pigpio.pi()        # connect to Pi
if not pi.connected:
   exit()
pi.set_mode(FLOW_ch, pigpio.INPUT)
pi.set_pull_up_down(FLOW_ch, pigpio.PUD_UP)
callback = pi.callback(FLOW_ch) # default tally callback


# Global variables
analog_sensor = None   # for thread of analog sensors
analogTread_flag = False

d_temp_sensor = None   # for thread of temperature sensors (digital)
tempTread_flag = False

global zerou, zeroi, zerod  # to zeroing the piezometric pressures (datum)


def init(interval, no_reads, flowmeter):
    global analog_sensor
    global d_temp_sensor
    global pulses, flowrate
    global v1,v2,p

    pulses   = 0      #starts the counting of pulses of the turbine flowmeter
    flowrate = 0      #starts the counting of the flowrate of the eletromagnetic flowmeter

    sleep = interval / no_reads

    #create the threads ('parallel' calculations for analog sensors and temp sensors)
    global tempTread_flag
    if tempTread_flag == False:  # avoids having multiple threats d_temp_sensor running
        d_temp_sensor = D_Temp(interval - 0.1)  # the sensor takes +-0.750s to read. so it's placed in a thread)
        d_temp_sensor.name = "dig temp sensors"  #give a name to thread for better debugging
        d_temp_sensor.start()
        tempTread_flag = True

    global analogTread_flag
    if analogTread_flag == False:  # avoids having multiple threats analog_sensor running
        analog_sensor = AnalogSensor(sleep,no_reads)  # average readings in the analog sensors per measure interval for signal stability)
        analog_sensor.name = "analog_sensors"
        analog_sensor.start()
        analogTread_flag = True

    if flowmeter == "1": # 1= eletroMagnetic flowmeter; 2 = turbine flowmeter
        # create a process only to read the eletromagnetic flowmeter
        # first see if any process to read the eletromag flowmeter is running and, if so, terminates it.
        try:
            p.terminate()
        except: pass

        v1 = multiprocessing.Value('d', 0.0)  # flow rate -> value for shared memory between parent(main)
        v2 = multiprocessing.Value('d', 0.0)  # total volume -> value for shared memory
        p = multiprocessing.Process(target=FlowMAG.read_flowMAG, args=(v1,v2,)) # parallel process
        p.start()


def zero_press(mu, mi, md, bu, bi, bd, testtype):
    # Transform the analog numbers in volts  # 15 bit value
    volts  = [0]*3
    zerou  = zeroi = zerod = 0 # values to zero pressure sensors - datum
    analog = [0]*3
    for ch in range(3):
        analog[ch] = adc.read_adc(ch, gain=GAIN, data_rate=DATA_RATE)
        # transform the analog number in volts
        # Ratio of 15 bit value to max volts determines volts
        volts[ch] = analog[ch] / 32767.0 * max_VOLT
        #determine the value to add in order to zero pressures
        zerou = (mu * volts[PRESSUP_ch] + bu)
        if testtype == '3':  # if the test is a HET (there is no intermediate pressure sensor)
            zeroi = 0
        else:
            zeroi = (mi * volts[PRESSINT_ch]+ bi)
        zerod = (md * volts[PRESSDW_ch] + bd)
    sleep(1)  # waits a second
    return zerou, zeroi, zerod

def get_data(interval, mu, mi, md, bu, bi, bd, zerou, zeroi, zerod, testtype, flowmeter, cf): #
    """Get the data from the sensors, also get the date and time.

    Data recorded:
        time (str): the time of the record in HH:MM:SS format.
        date (str): the date of the record in DD-MM-YYYY format.
        mmH2O_up (float): pressure in the upstream piezometer in mmH2O
        mmH2O_int (float): pressure in the piezometer at the interface (middle) in mmH2O
        mmH2O_dwn (float): pressure in the downstream piezometer in mmH2O
        flowrate (float): instantaneous flowrate in L/hour
        total_liters (float): Volume of fluid since start of program in Liters
        turb (int): the analog value of the turbidity (from 0 to 32768).
        water_temp (float): the temperature of the water in Celsius.
        air_temp (float): the ambient temperature in Celsius.
        air_hum (float): the ambient humidity in %
        air_pres (float): the barometric pressure in hectoPascal (around 1000 hPa).

    Returns:
        dict: The data in the order of the fieldnames.

    """
    global analog_sensor
    global d_temp_sensor
    global pulses, flowrate
    global v1,v2,p

    # Date (DD-MM-YYY) and time (HH:MM:SS)
    d = datetime.now()
    time_ = '{:%H:%M:%S}'.format(d)
    date_ = '{:%Y-%m-%d}'.format(d)

    # (DS18B) Water temperature + BME280
    water_temp, air_temp, air_hum, air_pres = d_temp_sensor.read_d_temp()

#FLOWMETERS
    if flowmeter == "1": # if eletromagnetic flowmeter is selected
        #flowmeter: MAGFLOW (eletromagnetic flowmeter).
        # Gets values from the parallel process which are in shared memory
        flowrate = v1.value  # in liters per hour
        total_liters = v2.value  # in liters

    else:  # Attention: if any other value rather than "1" is introduced in .ini file, then the program considers the turbine flowmeter!
        #flowmeter: turbine
        if cf == "": cf="0.45" # in case the cf variable is not set in ini file
        pulses_last = pulses
        pulses = callback.tally()
        total_liters = (pulses) / (float(cf)*60)  # 1L water = 0.45 x 60 = 27 pulses (device specs)
        flowrate = ((pulses - pulses_last) / interval / float(cf))*60  # f (Hz) = cf x Q , with Q = L/min  (cf = 0.45 device specs)


    # Transform the analog numbers in volts
    volts = [0] * 3
    bar   = [0] * 3
    mmH2O = [0] * 3
    bar_to_mmH2O = 10197.162129779283
    analog = analog_sensor.read_analog()  # get the actual reading from average

    for ch in range(0,3,1):
        if analog[ch] != 32767:  # The pcb has a pull-up resister that is used to check if there is no sensor attached.
        # Ratio of 15 bit value to max volts determines volts
            volts[ch] = analog[ch] / 32767 * max_VOLT
        else:
            volts[ch] = 0  # only pull-up resistor is present

    # linear relationship between psi & voltage in the pressure sensors(from manufacturer)
    if volts[PRESSUP_ch] != 0:
        bar[PRESSUP_ch] = (mu * volts[PRESSUP_ch]  + bu) - zerou # 0 psi(bar) = 0.5v ; 15psi(*psi_to_bar) = 4.5V
    else:
        bar[PRESSUP_ch] = 0
    if volts[PRESSINT_ch] != 0:
        bar[PRESSINT_ch] = (mi * volts[PRESSINT_ch] + bi) - zeroi  # 0 psi(bar) = 0.5v ;  5psi(*psi_to_bar) = 4.5V
    else:
        bar[PRESSINT_ch] = 0
    if volts[PRESSDW_ch] != 0:
        bar[PRESSDW_ch] = (md * volts[PRESSDW_ch]  + bd) - zerod # 0 psi(bar) = 0.5v ;  5psi(*psi_to_bar) = 4.5V
    else:
        bar[PRESSDW_ch] = 0

    for ch in range(3):
        if volts[ch] != 0:
            mmH2O[ch] = bar[ch] * bar_to_mmH2O   # mmH2O conversion
        else:
            mmH2O[ch]=0
    if testtype == '3':             #HET
        volts[PRESSINT_ch]= 0
        bar[PRESSINT_ch]= 0
        mmH2O[PRESSINT_ch]= 0

    turb_analog = analog[TURB_ch]           # analog 0 to 32767


    if turb_analog != 32767:  # value given by pull-up resistor -> nothing connected
        turb = turbidity_calibration.turb_interpolate(turb_analog)
        turb=float(turb)
    else:
        turb = 0


    return {
        'date':         date_,
        'time':         time_,
        'v_up':         volts[PRESSUP_ch],  #V
        'v_int':        volts[PRESSINT_ch], #V
        'v_down':       volts[PRESSDW_ch],  #V
        'bar_up':       bar[PRESSUP_ch],    #bar
        'bar_int':      bar[PRESSINT_ch],   #bar
        'bar_down':     bar[PRESSDW_ch],    #bar
        'mmH2O_up':     round(mmH2O[PRESSUP_ch]),
        'mmH2O_int':    round(mmH2O[PRESSINT_ch]),
        'mmH2O_down':   round(mmH2O[PRESSDW_ch]),
        'ana_turb':     round(analog[TURB_ch]), #analog number
        'turb':         round(turb,3),
        'flow':         round(flowrate,2),
        'liters':       round(total_liters,2),
        'water_temp':   round(water_temp,1),
        'air_temp':     round(air_temp,1),
        'air_hum':      round(air_hum,1),
        'air_pres':     round(air_pres),

    }

#for testing
#init(5,1)
#get_data(5,.4,.4,.4,.4,.4,.4,.4,.4,0.01,0.01,0.01,1) #( dummy values )

#
#     callback.cancel()  # cancel callback
#     pi.stop() # disconnect from Pi
#
#     print("\nexiting")
#     end(RUN_TIME)
#     os._exit(0)

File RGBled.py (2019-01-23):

#! /usr/bin/python3
# -*- coding: utf-8 -*-
#Ricardos.geral@gmail.com


import RPi.GPIO as GPIO
from time import sleep
redPin = 16    # GPIO16 pin 36
greenPin = 21  # GPIO21 pin 40
bluePin = 12   # GPIO12 pin 32


def blink(pin):
    GPIO.setmode(GPIO.BCM)
    GPIO.setwarnings(False)
    GPIO.setup(pin, GPIO.OUT)
    GPIO.output(pin, GPIO.HIGH)

def turnOff(pin):
    GPIO.setmode(GPIO.BCM)
    GPIO.setup(pin, GPIO.OUT)
    GPIO.output(pin, GPIO.LOW)

def redOn():
    blink(redPin)

def redOff():
    turnOff(redPin)

def greenOn():
    blink(greenPin)

def greenOff():
    turnOff(greenPin)

def blueOn():
    blink(bluePin)

def blueOff():
    turnOff(bluePin)

def yellowOn():
    blink(redPin)
    blink(greenPin)

def yellowOff():
    turnOff(redPin)
    turnOff(greenPin)

def cyanOn():
    blink(greenPin)
    blink(bluePin)

def cyanOff():
    turnOff(greenPin)
    turnOff(bluePin)

def magentaOn():
    blink(redPin)
    blink(bluePin)

def magentaOff():
    turnOff(redPin)
    turnOff(bluePin)

def whiteOn():
    blink(redPin)
    blink(greenPin)
    blink(bluePin)

def whiteOff():
    turnOff(redPin)
    turnOff(greenPin)
    turnOff(bluePin)

def shutdown_led(): #10 fast red flashes
    for i in range(10):
        redOn()
        sleep(0.1)
        redOff()
        sleep(0.1)

def reboot_led(): #10 fast blue flashes
    for i in range(10):
        blueOn()
        sleep(0.1)
        blueOff()
        sleep(0.1)

def main():
#print("""Ensure the  GPIO connections are correct
#Colors: Red, Green, Blue, Yellow, Cyan, Magenta, and White
#Use the format: color on/color off""")
    while True:
        cmd = input("-->")

        if cmd == "red on":
            redOn()
        elif cmd == "red off":
            redOff()
        elif cmd == "green on":
            greenOn()
        elif cmd == "green off":
            greenOff()
        elif cmd == "blue on":
            blueOn()
        elif cmd == "blue off":
            blueOff()
        elif cmd == "yellow on":
            yellowOn()
        elif cmd == "yellow off":
            yellowOff()
        elif cmd == "cyan on":
            cyanOn()
        elif cmd == "cyan off":
            cyanOff()
        elif cmd == "magenta on":
            magentaOn()
        elif cmd == "magenta off":
            magentaOff()
        elif cmd == "white on":
            whiteOn()
        elif cmd == "white off":
            whiteOff()
        else:
            print("Not a valid command")

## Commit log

2018-05-03 Add files via upload
    first commits
    [erosion_v3_contour.gm1, erosion_v3_copperBottom.gbl, erosion_v3_copperTop.gtl, erosion_v3_maskBottom.gbs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]
2018-05-03 update ignorelist
    [erotes_production.fzz]
2018-05-04 Readme update
    [erotes_production.fzz]
2018-05-07 Make gain and correspondent voltage more less prone to error of user
2018-05-10 update name
    [relier_production.fzz, relier_production_contour.gm1, relier_production_copperBottom.gbl, relier_production_copperTop.gtl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]
2018-06-01 Ensure that total volume is 0 at start of tests
    [relier_production.fzz]
2018-06-29 add connection to heroku
    [relierv2_production_test.fzz]
2018-07-04 change shutdown pin button
2018-07-06 put RGB led working
2018-07-06 correct buzer pin
2018-07-12 correct turbidity to g/cm3 and logaritmic calibration
2018-07-18 correct turbidity to g/cm3 and logaritmic calibration 3D print files
    [turbidity_v1.blend, turbidity_v1.stl]
2018-07-19 Media files (images)
    [Calibration.xlsx]
2018-08-16 turbidity bug in google docs corrected
    [Calibration.xlsx, turbidity_v2.blend, turbidity_v2_1.blend, turbidity_v2_1.stl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]
2018-08-28 pins # correction Flow 27 to 25 temp 4 to 24 shutdown button 17 to 23
2018-08-28 pins # correction blue pin 26 to 12
    [relierv3_production(hat).fzz]
2018-11-09 change pcb to v3.1
    [Enclosure box_openings.dwg, relierv3.1_production(hat).fzz, relierv3.1_production(hat)_contour.gm1, relierv3.1_production(hat)_copperBottom.gbl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]
2018-11-14 make sure DATARATE in ADS1115 is the same in both files "sensor_server.py" and "analogsensor_thread.py"
2018-11-19 Implementation of a ring buffer in the thread of the analog readings
2018-11-20 detects if no sensor is attached in ADC pins (because of pull-up resistors)
2018-11-21 added pull-up resistors in fritzing
    [relierv3.2_production(hat).fzz, relierv3_production(hat).fzz]
2018-11-30 implementation of the possibility to choose the flowmeter type: 1 - eletromagnetic; 2 - turbine
2018-11-30 try to reconnect if FLOWMAG is not connected to USB serial port
2018-12-03 decimal points in flow volume and flow rate in liters/hour in turbine flowmeter
2018-12-04 implementation of calibration of turbidity using a txt file
    [Calibration.xlsx]
2018-12-05 save inputs in inputs.ini file after return button in sensors page
2018-12-06 put current flow rate in sensors page
    [Calibration.xlsx, relierv3.2_production(hat).fzz]
2018-12-07 ensure that flowrate is updated if the flowtype button is selected
2018-12-10 calibration of turbidity (ODL soil)
    [Calibration_1.xlsx]
2018-12-10 make sure that serial connection with FlowMag occurs right from start
2018-12-14 put option -y in install batch
    [Calibration_1.xlsx]
2018-12-19 README update In set sensors interval is set always to 1 second (but number of readings is not changes)
2019-01-04 correct 1wire GPIO to pin 24 in Raspberry
2019-01-09 round units for turbine flowmeter
2019-01-10 round flow liters to 1 decimal place
2019-02-20 implementation of endoscopic camera shots during record
2019-02-22 camera endoscopic timelapse feature
2019-02-25 camera endoscopic timelapse feature minor bug fix
